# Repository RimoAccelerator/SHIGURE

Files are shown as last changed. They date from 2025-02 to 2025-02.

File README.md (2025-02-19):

# SHIGURE：一款开源的在线控制注射泵

## 背景和原理

输液泵是实验室自动化中最基础的部件之一，而注射泵是所有泵中最容易DIY的（虽然成本不一定最低）。市场上注射泵的价格在500~1000+ RMB左右，相比之下DIY的注射泵更有性价比，不仅能实现相似的功能，还有灵活得多的控制方式，可适配多种自定义的用途。SHIGURE是开源的在线控制注射泵，遵循如下步骤，每个人都能组装出一台可以同时使用Wifi和串口方式控制的注射泵，并且借助客户端可以实现复杂的流程控制、甚至多泵协同工作。

注射泵的核心部件是步进电机和丝杆滑台。步进电机在接收脉冲后旋转，通过丝杆滑台转化为线性位移，只需用固定件将注射器固定在滑台上即可。为了能兼容往复运动以及不同规格和含有不同量液体的注射器，设计了一个用4组螺杆和8个手拧螺母的调节机构，可以在前后上下方向改变注射器卡口的位置。

为了控制步进电机，使用树莓派Pico发送PWM脉冲给TMC2209控制模块后驱动电机运动。在丝杆滑台两端设置限位开关，当滑块运动到尽头时及时停止运动。

为了实现对硬件的操纵，使用带有Wifi功能的树莓派Pico W，同时允许串口控制。

## 目录结构

Models： 3D打印PCB外壳文件；各固定件的图纸文件；

PCB：嘉立创EDA的项目文件和Gerber文件；

ShigureController：控制软件代码；

shigure_main.py：树莓派pico上的micropython代码。

## 精度参数

| 注射器（mL) | 最小流速 （mL/min) | 最大流速 （mL/min) | 流速精度 |
| ------- | ------------- | ------------- | ---- |
| 30      | 0.51          | 200           | ±5%  |
| 10      | 0.20          | 80            | ±3%  |
| 5       | 0.15          | 50            | ±1%  |
| 1       | 0.03          | 10            | ±1%  |

## 物料和成本

以下为直接采购的物料：

| 物料            | 数量  | 型号/供应商                    | 单个成本 (RMB) |
| ------------- | --- | ------------------------- | ---------- |
| 丝杆滑台          | 1   | 1204/100 mm 东台市欧力传动部件有限公司 | 150        |
| 限位开关          | 2   | NPN 海杰嘉创行星减速机工厂           | 15         |
| 树莓派Pico W     | 1   | -                         | 52         |
| TMC2209模块     | 1   | 同拓展志                      | 14         |
| M4螺丝          | 4   | -                         | -          |
| M4螺柱          | 4   | -                         | -          |
| 手拧螺母（羊角）      | 4   | -                         | -          |
| 手拧螺母（圆形）      | 4   | -                         | -          |
| 1 k电阻         | 5   | -                         | -          |
| 二极管           | 2   | IN4148                    | -          |
| LED           | 2   | -                         | -          |
| CH340串口转USB模块 | 1   | -                         | 6          |
| 导线、连接座        | 若干  | -                         | -          |

以上各部件均来自淘宝。树莓派Pico W必须使用原版。

需要制作4个固定件，参考成本：嘉立创3D打印，约25元；嘉立创钣金加工，约70元。

## 机械部分装配过程

1. 打印零件
   
   固定件1
   
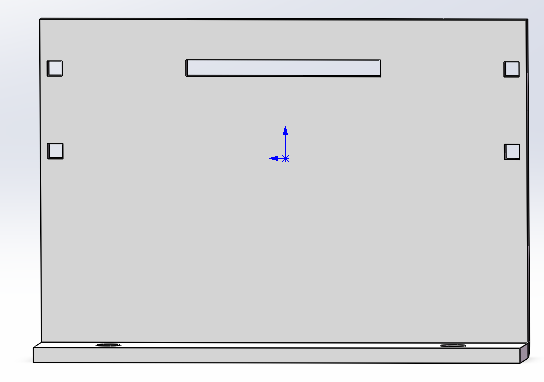
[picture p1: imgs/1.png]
   
   
   固定件2（互为镜像的一对，以下只展示一个）
   
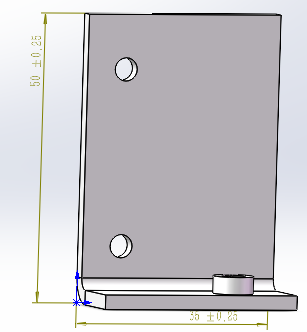
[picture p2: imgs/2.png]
   
   
   固定件3
   
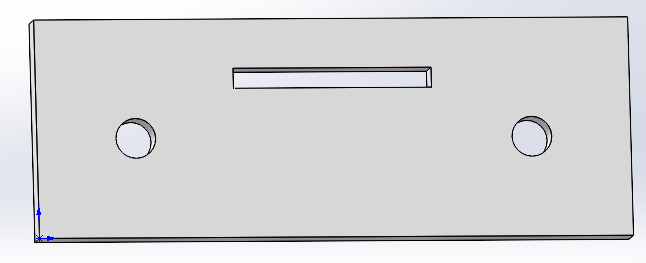
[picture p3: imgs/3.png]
   
   
   固定件4
   
   
   
   关于孔大小：
   
   * 所有孔均设计为M4尺寸。在图纸中，孔直径按照3.3 mm画，如果进行CNC加工可以自动识别为M4螺丝座。如果是3D打印，需将孔直径改成合适的值（至少是4 mm）。
     
     其中固定件4要特别说明。固定件4上的2个螺纹孔位需要插入M4螺柱，且上下没有螺母紧固，需要自身螺纹将螺柱咬住。这是所有打印件里唯一对孔大小有较严格要求的部分。如果使用3D打印加工，图纸上的孔位半径需要根据打印机状态调整，适应公差。例如，开发者自有的3D打印机打出来的孔负公差很大，而嘉立创的3D打印则公差较小。对于前者，此处孔径需要设计为4.4 mm左右，而对于后者可设计为3.8 mm左右，需要尝试和经验。好在对于树脂3D打印器件，无论孔是开得偏大还是偏小都有手动处理的办法，如果孔太大可以用热熔胶将螺柱粘上去，如果孔太小可以用火烧一烧。

2. 安装限位开关
   
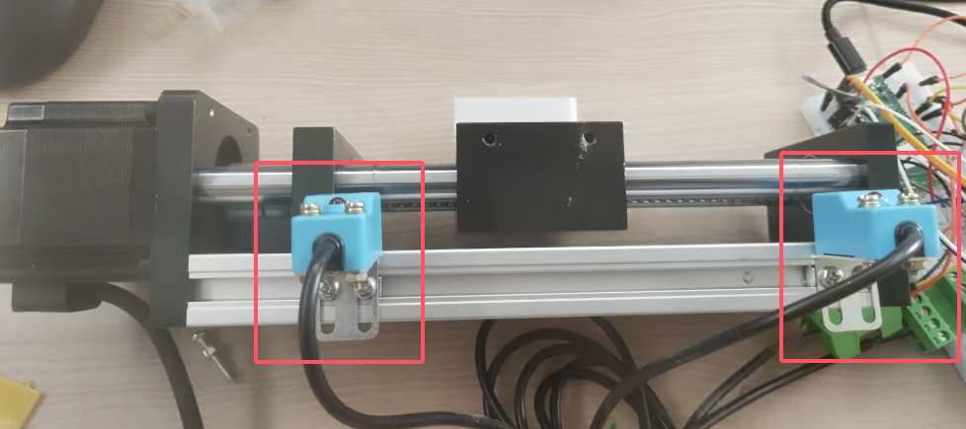
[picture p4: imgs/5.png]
   

3. 安装固定件1，将螺丝打在电机一侧固定端的孔位，在外侧以螺母固定，并利用两侧的孔位安装弹簧。图纸中设计了2个弹簧孔位，至少要在顶部与注射器卡槽平齐的一组安装弹簧。
   
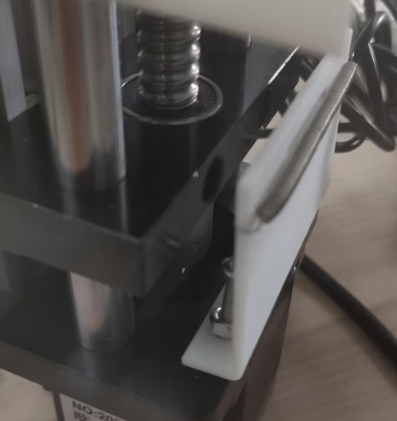
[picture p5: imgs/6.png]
   

4. 在丝杆滑台侧面安装固定件2，将螺丝打进滑块侧面的孔位，在外侧以螺母固定。
   
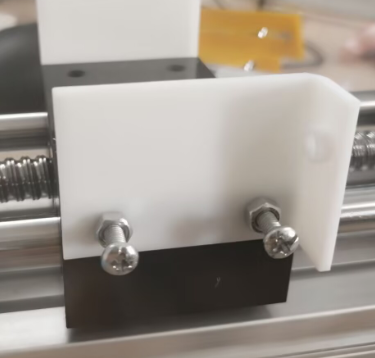
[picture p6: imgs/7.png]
   

5. 通过固定件2，插入M4螺柱，在靠内侧一端以螺母固定，靠外侧一端放入圆形手拧螺母。随后在螺柱上安装固定件4，外侧以羊角手拧螺母固定。这里螺柱的作用是调节注射器活塞卡口位置以适配各种型号、或存有各种体积液体的注射器，因此可以选用足够长的螺柱。作为演示，此处使用了短螺柱。
   
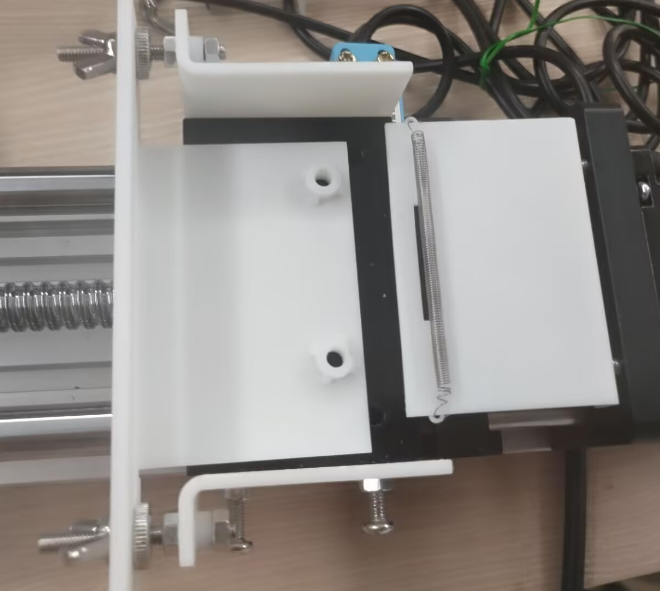
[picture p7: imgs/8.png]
   

6. 在固定件4的两个空位上插入M4螺柱，不使用螺母固定。在螺柱上依次放入圆形手拧螺母、固定件3、羊角手拧螺母。放入注射器，通过调节4组手拧螺母可改变固定件3和4的位置以适应注射器长度和高度。
   
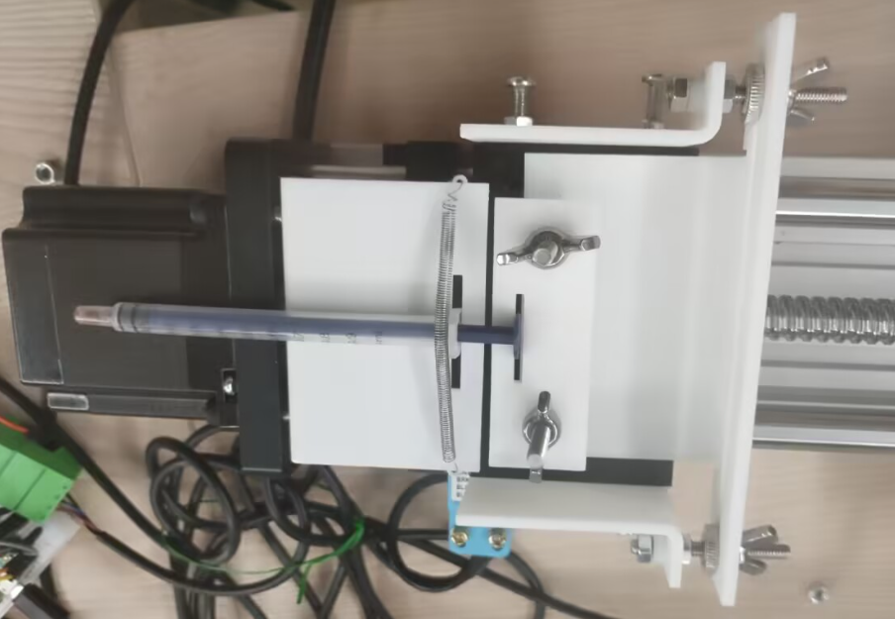
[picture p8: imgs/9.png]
   
   
   以下是使用钣金件的版本，强度更高：
   
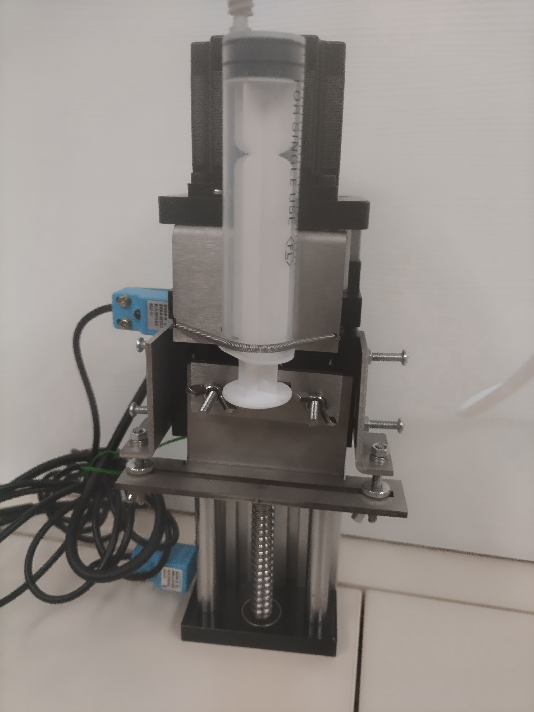
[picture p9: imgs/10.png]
   
   
   ## 电子部分
   
   使用树莓派Pico W进行控制，利用TMC2209驱动电机。以下为原理图：
   
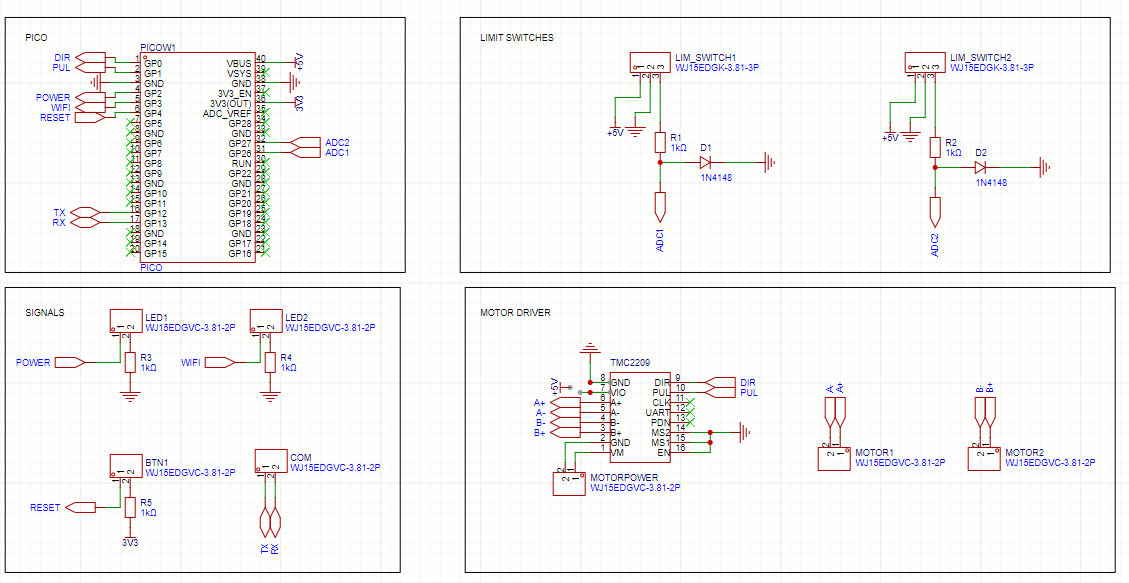
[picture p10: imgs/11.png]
   
   
   TMC2209模块采用Pico的5 V供电，57步进电机使用12 V/2 A的电源。电机电源线和4个线圈连线接在TMC2209上。Pico的GPIO0和1分别用作DIR和PUL，GPIO2~4分别用于控制电源指示灯、控制WIFI指示灯和接收开关按键信号。GPIO12和13留作与上位机通信的串口接口。
   
   两个限位开关使用5 V供电，两个限位开关平时输出5 V电压，在滑块靠近时输出0 V。由于Pico不能直接读取5 V电平，使用二极管钳位电路将限位开关输出的5 V转化为大约0.7 V电位后，通过GPIO26和27进行ADC读取。当这两个引脚的输入电压低于0.5 V时，判定为滑块接近限位开关，停止滑块运动。
   
   在面包板上的连接相对而言是比较简单的：
   
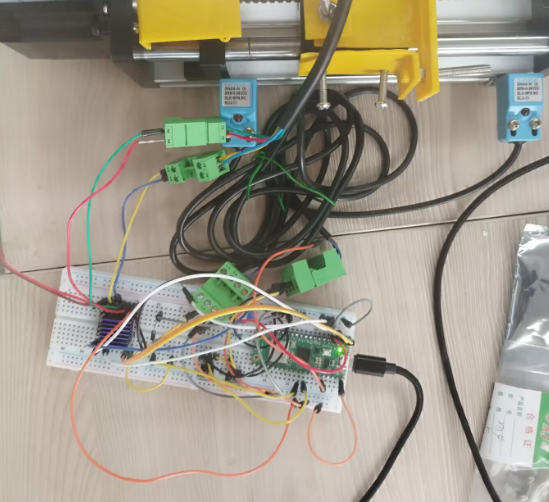
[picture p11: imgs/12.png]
   
   
   以上电路可以转移到一个7.2 * 7.0 cm2的PCB板上：
   
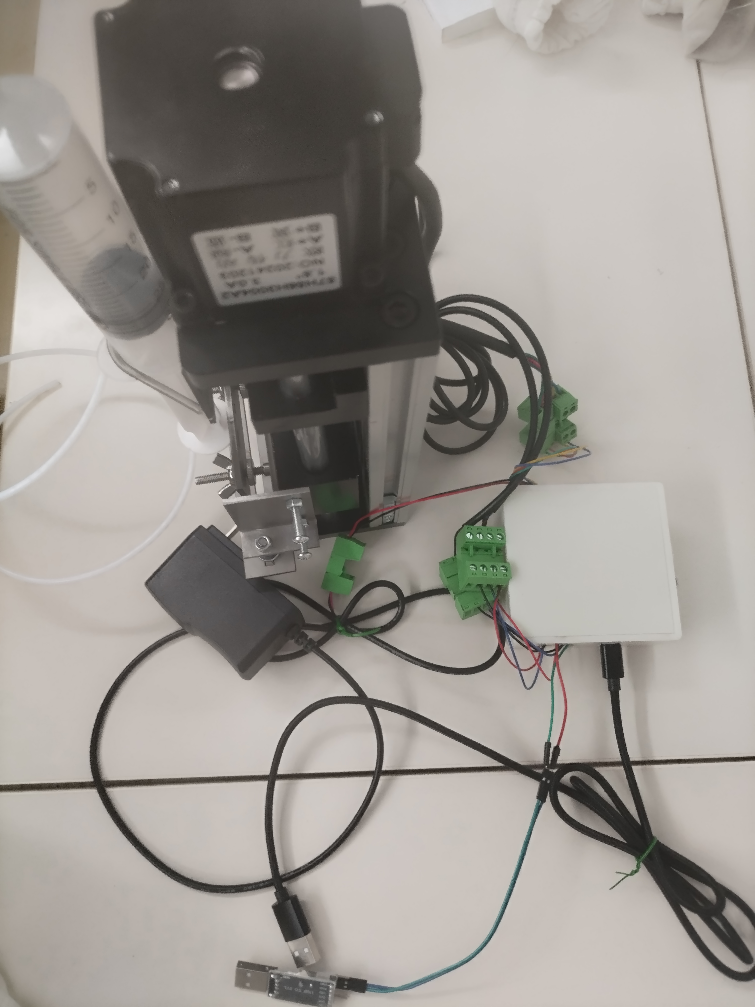
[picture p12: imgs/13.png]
   

## 操作过程

### AP模式

SHIGURE第一次运行时，Wifi处于未配置状态。开始运行后，GP2连接的电源LED亮起，GP3连接的Wifi LED不亮，程序处于AP模式，将产生一个以PumpXX为名称的Wifi信号，其中XX是100以内的随机数。连接这个Wifi（密码是bsjinstrument）后，访问192.168.4.1，进入注射泵控制页面。

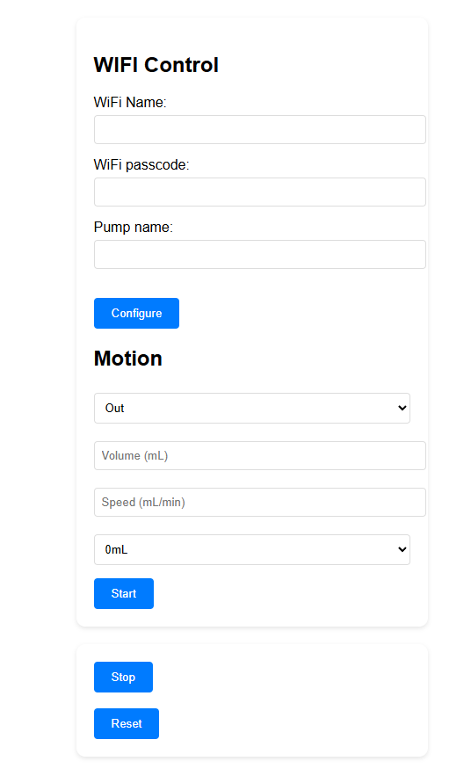
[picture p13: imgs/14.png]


在这一页面，可以输入Wifi信息，点击Configure，则机器将Wifi信息写入存储中并自动重启连接该Wifi，进入Wifi模式，此时GP4连接的Wifi LED亮起。Pump name可以自定义。机器连接Wifi后，AP模式同样可以使用，与此同时，同Wifi内的设备也可以访问注射泵。

如果需要重置，可以长按开关3 s。如果短按，则设备会重启但不重置。

### 网页控制

在网页内的Motion模块，可以选择注射器型号、设置体积和流速。In和Out分别对应吸液和推液。点击Reset后，SHIGURE会推出液体，直到达到限位开关位置。

如果注射器规格选择0 mL，则Volume和Speed分别表示移动的距离（mm）和速度（mm/min)。

### 客户端控制

Wifi模式中，注射泵连接Wifi并获得IP地址。输入注射泵的IP地址后，可以打开相同页面。但一般用户不容易知道注射泵的IP地址，ShigureController客户端提供了控制局域网内所有注射泵的平台。

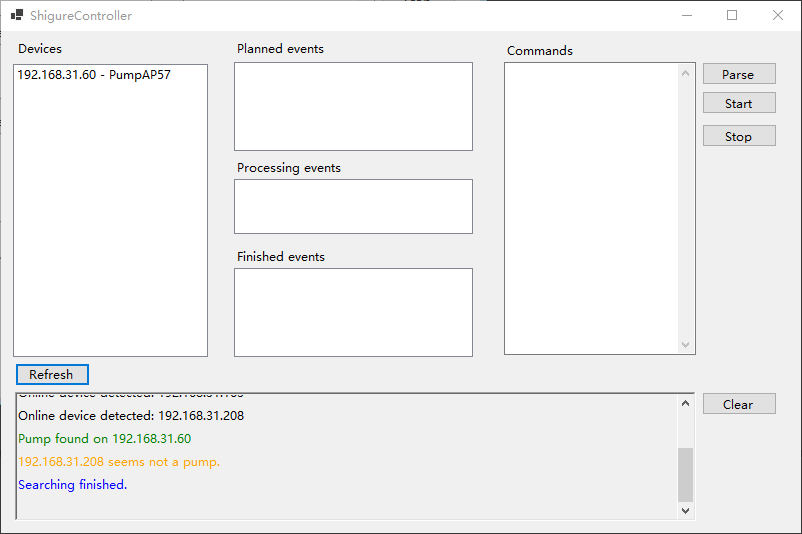
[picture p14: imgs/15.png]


运行ShigureController后，程序会自动搜索局域网内的设备，将注射泵的IP和名称列出。用户在Commands里，按照如下格式输入命令：

```
set ID xx #为相应ID的泵设置注射器规格为xx mL
move ID direction volume speed
    #让相应ID的泵按照给定方向（in或out）以指定流速（mL/min）运行指定体积（mL）
pause ID xx #让相应ID的泵停止xx min
```

以下是一个例子：

```
set PumpAP57 30
move PumpAP57 out 10 200
move PumpAP57 in 10 200
pause PumpAP57 0.1
move PumpAP57 out 10 200
```

在这个例子中，PumpAP57采用30 mL注射器，先以200 mL/min打出10 mL，再吸入10 mL，暂停6 s后再打出10 mL。为了兼容网络延迟，使用客户端控制时，每两个动作之间会有一段3 s的暂停。

当存在多个泵时，可以用类似的方法控制每个泵实现协同工作。（但目前未测试过多泵协同，这是由于只组装了一台）

在输入命令后，首先点击Parse，则这些事件规划进入到Planned events中：

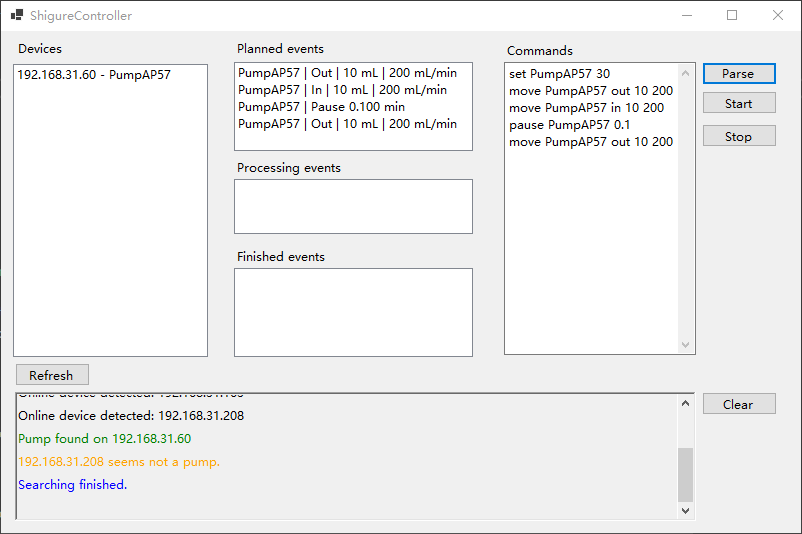
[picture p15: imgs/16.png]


然后点击Start，开始依次执行：

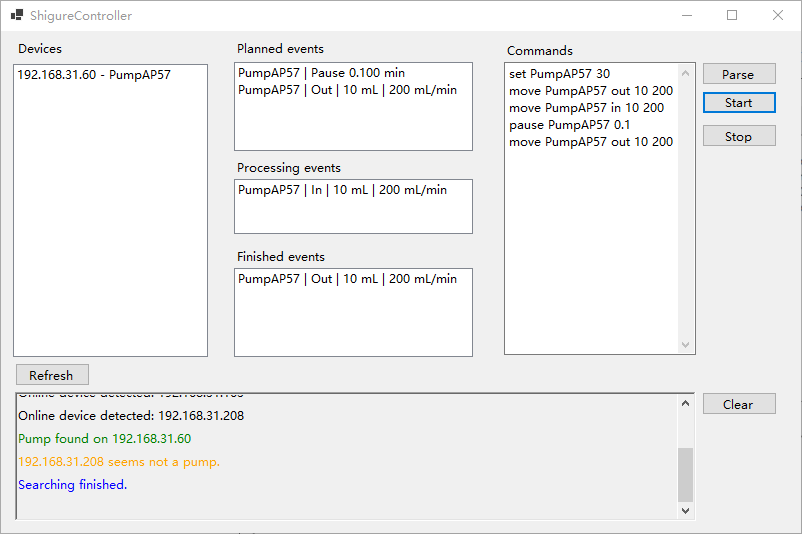
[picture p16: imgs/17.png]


执行完成后，所有事件都将进入到Finished events中。当然也可以随时点击Stop停止流程。

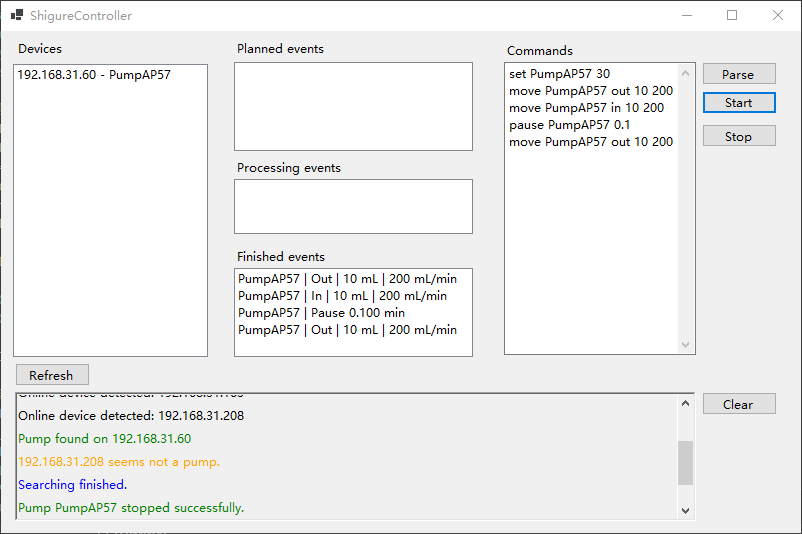
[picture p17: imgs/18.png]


### 串口控制

除了网络控制外，SHIGURE预留了串口线，可以同时接受串口信号，但不会返回信号。波特率采用9600，通信格式为： 

```
set syringe XX #设置注射器规格为XX mL
move direction volume speed 
    #按照给定方向（in或out）以指定流速（mL/min）运行指定体积（mL）
stop #停止
reset #重置
```

## 关于

SHIGURE是BSJ INSTITUTE开发的第二款开源硬件。我们将推出更多开源硬件，推动科学研究的普及化和自由化。

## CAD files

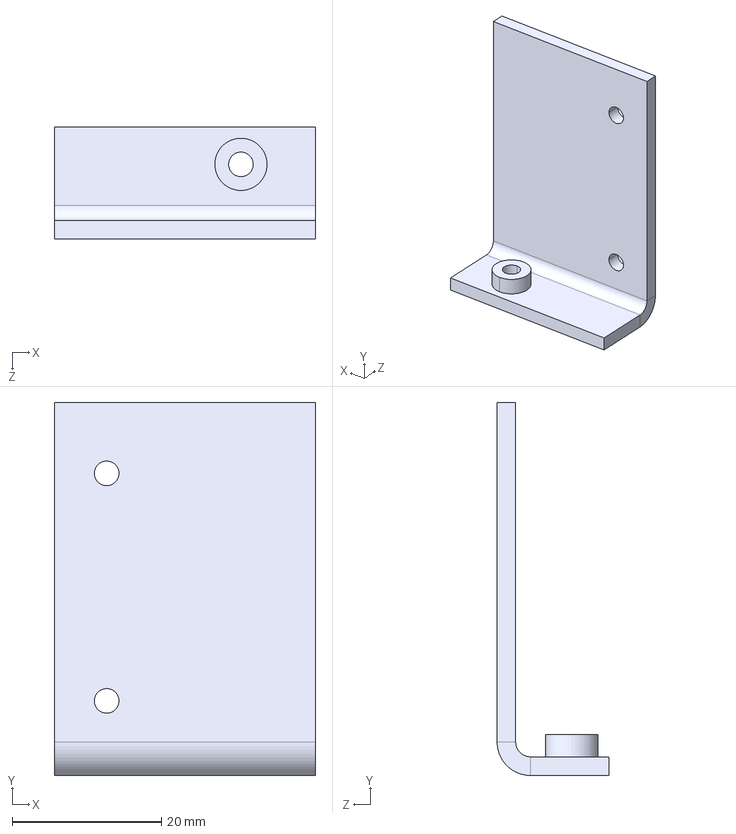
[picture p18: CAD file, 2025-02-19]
a/Models/Mirror_Fixture2.STEP
35.0 x 50.0 x 15.0 mm

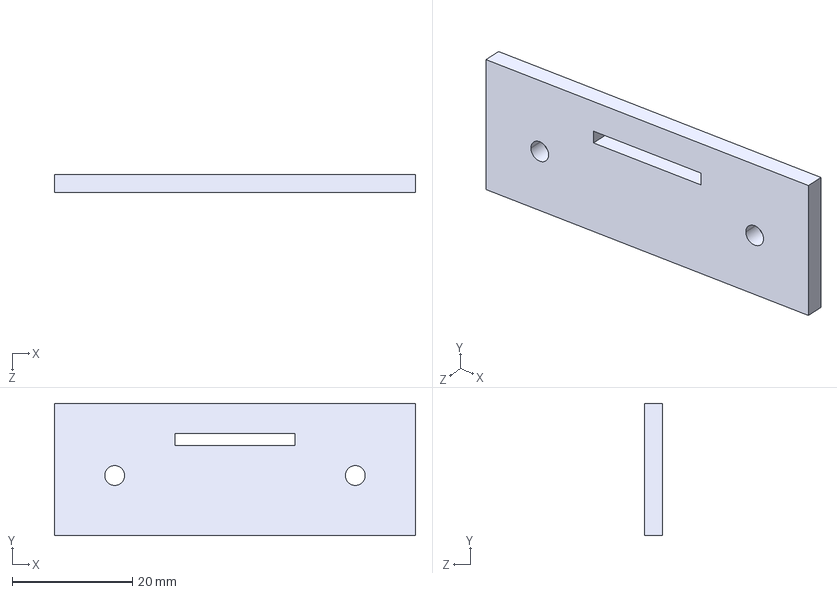
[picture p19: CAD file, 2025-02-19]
Models/Fixture3.STEP
60.0 x 22.0 x 3.00 mm

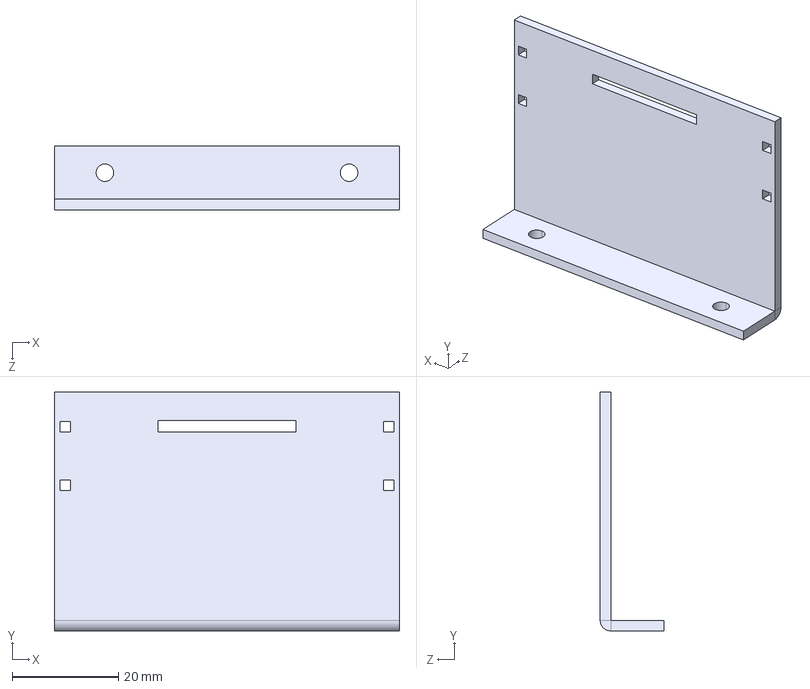
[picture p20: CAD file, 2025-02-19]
a/Models/Fixture1.STEP
65.0 x 45.0 x 12.0 mm

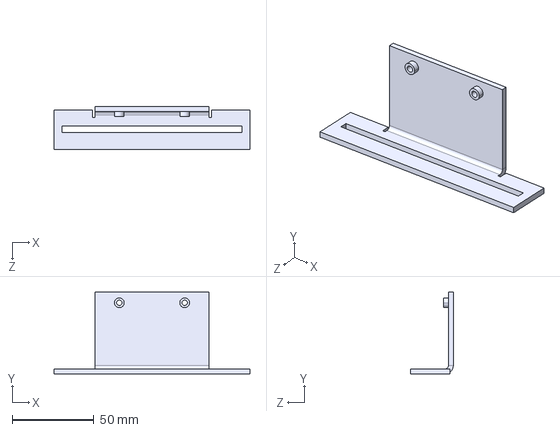
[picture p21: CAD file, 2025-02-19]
a/Models/Fixture4.STEP
120.0 x 50.0 x 26.1 mm

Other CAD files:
a/Models/Fixture2.STEP
Models/Fixture2.STEP
Models/Fixture1.SLDPRT
Models/Fixture2.SLDPRT
Models/Fixture3.SLDPRT
Models/Fixture4.SLDPRT
Models/Mirror_Fixture2.SLDPRT
a/Models/Fixture1.SLDPRT
a/Models/Fixture2.SLDPRT
a/Models/Fixture3.SLDPRT
a/Models/Fixture4.SLDPRT
a/Models/Mirror_Fixture2.SLDPRT

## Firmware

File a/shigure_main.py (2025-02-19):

import network
import machine
import os
import ujson
from machine import Pin, ADC, PWM
import utime
import socket
import ure
import random
import select
import sys
import uselect

# 硬件配置 ====================================================
MOTOR_DIR = Pin(0, Pin.OUT)
MOTOR_PUL = Pin(1, Pin.OUT)
PWM_PUL = PWM(MOTOR_PUL)
PWM_PUL.duty_u16(0)  # 50% duty cycle
PWM_PUL.freq(1000) 
LED_POWER = Pin(2, Pin.OUT)
LED_WIFI = Pin(3, Pin.OUT)
LED_BOARD = Pin("LED", Pin.OUT)

POS_SENSOR1 = ADC(Pin(26))
POS_SENSOR2 = ADC(Pin(27))

SWITCH_PIN = Pin(4, Pin.IN, Pin.PULL_DOWN)

# 运动参数 =====================================================
MICROSTEP = 1
DISTANCE_PER_REV = 0.4 * 1.2  # mm, 1.2 is determined by the actual measurement
STEPS_PER_REV = 200
MAX_SPEED = 500  # mm/min
SYRINGE_PROFILES = {
    0 : 0, 1 : 4.74, 5 : 12.6, 10 : 15.17, 30 : 23.6  # 注射器直径(mm)
}
SYRINGE = 30 # default syringe size
DIRECTION_PULL = 0
DIRECTION_PUSH = 1

# 全局状态 =====================================================
class State:
    IDLE = 0
    MOVING = 1
    STOPPING = 2

motor_state = State.IDLE
frequency = 0
motion_time = 0 # motion time in seconds
start_time = utime.ticks_ms()
direction = DIRECTION_PUSH
emergency_stop = False
switch_pressed_time = 0

# WiFi配置 =====================================================
WIFI_SSID = ''
WIFI_PWD = ''
HOST_NAME = 'PumpAP' + str(random.randint(0,100))
AP_CONFIG = (HOST_NAME, 'bsjinstrument')
CONFIG_FILE = 'wifi.json'

# 电机控制函数 =================================================
def update_motor():
    global motor_state, current_steps, last_step, emergency_stop
    if motor_state != State.MOVING:
        return
    # 碰撞检测
    if (direction == DIRECTION_PUSH and read_sensor(POS_SENSOR1)) or \
       (direction == DIRECTION_PULL and read_sensor(POS_SENSOR2)):
        emergency_stop = True
        print('Motion stopped because obstacle met')
    
    # 紧急停止或完成运动
    if emergency_stop:
        motor_state = State.STOPPING
        PWM_PUL.duty_u16(0)
        motor_state = State.IDLE
        print('Motion stopped because stop signal received')
        emergency_stop = False
        return
    
    # 步进脉冲生成
    now = utime.ticks_ms()
    if utime.ticks_diff(now, start_time) > motion_time * 1000:
        motor_state = State.STOPPING
        PWM_PUL.duty_u16(0)
        motor_state = State.IDLE
        print('Motion stopped because target reached')
        return


def read_sensor(sensor):
    return sensor.read_u16() * 3.3 / 65535 < 0.5 # Return True when sensor value is low, meaning obstacle detected

def calculate_motion(syringe, volume, speed):
    diameter = SYRINGE_PROFILES.get(syringe, 20)
    if syringe == 0:
        distance = volume
    else:
        area = 3.14159 * (diameter/2)**2  # mm²
        distance = (volume * 1000) / area  # mm 
    speed = distance / (volume / speed) / 60 # mm/s
    time = distance / speed  # s
    print(f'distance: {distance} mm, speed: {speed} mm/s, time: {time}')
    frequency = int(speed / DISTANCE_PER_REV * STEPS_PER_REV * MICROSTEP)  # Calculate frequency for PWM
    return frequency, time

def reset_motor():
    global motor_state, direction, frequency, motion_time, PWM_PUL, start_time
    motor_state = State.MOVING
    direction = DIRECTION_PUSH
    MOTOR_DIR.value(direction)
    motion_time = 20
    start_time = utime.ticks_ms()
    PWM_PUL.freq(2000)
    PWM_PUL.duty_u16(32768)

# 网络处理函数 =================================================
class WebServer:
    def __init__(self, ip):
        self.sock = socket.socket()
        self.sock.setsockopt(socket.SOL_SOCKET, socket.SO_REUSEADDR, 1)
        self.sock.bind(('0.0.0.0', 80))
        self.sock.listen(5)
        #self.sock.settimeout(0.1)
        self.sock.setblocking(False)
        self.routes = {
            r'GET /': self.handle_root,
            r'POST /move': self.handle_move,
            r'POST /stop': self.handle_stop,
            r'POST /reset': self.handle_reset,
            r'POST /configure': self.handle_configure
        }
        self.poll = select.poll()
        self.poll.register(self.sock, select.POLLIN)  # 使用poll机制
    
    def process(self):
        res = self.poll.poll(50)  # 50ms超时
        for sock, event in res:
            if sock == self.sock:
                try:
                    cl, addr = self.sock.accept()
                    cl.setblocking(False)
                    self.poll.register(cl, select.POLLIN)
                except OSError:
                    pass
            else:
                self.handle_client(sock)

    def handle_client(self, cl):
        try:
            request = cl.recv(1024).decode()
            if request:  # 确保收到有效请求
                self.handle_request(cl, request)
        except Exception as e:
            print('Client error:', e)
        finally:
            self.poll.unregister(cl)
            cl.close()
    
    def handle_request(self, cl, request):
        for pattern, handler in self.routes.items():
            if ure.match(pattern, request):
                return handler(cl, request)
        self.send_response(cl, "Not Found", status=404)
    
    def handle_root(self, cl, request):
        options = ''.join(f'<option value="{k}">{k}mL</option>' for k in sorted(SYRINGE_PROFILES))
        form = f"""
        <div class="card">
        <h2>WIFI Control</h2>
        <form action="/configure" method="post" enctype="application/x-www-form-urlencoded">
            <label for="ssid">WiFi Name:</label><br>
            <input type="text" id="ssid" name="ssid" value={WIFI_SSID}><br>
            <label for="password">WiFi passcode:</label><br>
            <input type="text" id="password" name="password" value={WIFI_PWD}><br>
            <label for="name">Pump name:</label><br>
            <input type="text" id="name" name="name" value={HOST_NAME}><br>
            <br>
            <button type="submit">Configure</button>
        </form>
          <h2>Motion</h2>
          <form action="/move" method="post" target="hidden-form">
            <select name="dir"><option value="1">Out</option><option value="0">In</option></select>
            <input type="number" name="vol" placeholder="Volume (mL)" step="0.01" required>
            <input type="number" name="speed" placeholder="Speed (mL/min)" min="0"  step="0.01" max={MAX_SPEED} required>
            <select name="syr">{options}</select>
            <button type="submit">Start</button>
          </form>
        </div>
        <div class="card">
          <form action="/stop" method="post" target="hidden-form"><button>Stop</button></form><br />
          <form action="/reset" method="post" target="hidden-form"><button type="button" onclick="this.form.submit()">Reset</button></form>
        </div>
        """
        self.send_response(cl, """<!DOCTYPE html>
<html><head>
<title>Pump Control</title>
<meta name="viewport" content="width=device-width, initial-scale=1">
<style>
  body{max-width:400px;margin:20px auto;padding:20px;font-family:Arial,sans-serif}
  .card{padding:20px;border-radius:10px;box-shadow:0 2px 5px rgba(0,0,0,0.1);margin-bottom:20px}
  input,select{width:100%;padding:8px;margin:5px 0 15px;border:1px solid #ddd;border-radius:4px}
  button{background:#007bff;color:white;border:none;padding:10px 20px;border-radius:4px;cursor:pointer}
  button:disabled{background:#6c757d}
</style>
</head><body><iframe style="display:none" name="hidden-form"></iframe>
""" + form + "</body></html>")
    
    def handle_move(self, cl, request):
        global motor_state, direction, frequency, motion_time, PWM_PUL, start_time, SYRINGE
        params = self.parse_params(request)
        try:
            SYRINGE = int(params.get('syr',20))
            volume = float(params.get('vol',0))
            speed = min(MAX_SPEED, float(params.get('speed',1)))
            direction = int(params.get('dir',0))
            print(f"Move: {direction}, {volume}mL, {speed}mL/min, {SYRINGE}mL syringe")
            frequency, motion_time = calculate_motion(SYRINGE, volume, speed)
            motor_state = State.MOVING
            MOTOR_DIR.value(direction)
            start_time = utime.ticks_ms()
            PWM_PUL.freq(frequency)
            PWM_PUL.duty_u16(32768)
            print(f'Moving: {frequency}Hz, {motion_time}s')
            self.send_response(cl, "Motion start")
        except Exception as e:
            self.send_response(cl, f"Parameter error: {str(e)}", status=400)
    
    def handle_configure(self, cl, request):
        global WIFI_SSID, WIFI_PWD, HOST_NAME
        params = self.parse_params(request)
        try:
            WIFI_SSID = params.get('ssid', '')
            WIFI_PWD = params.get('password', '')
            HOST_NAME = params.get('name', '')
            with open(CONFIG_FILE, 'w') as f:
                ujson.dump({'ssid': WIFI_SSID, 'password': WIFI_PWD, 'name': HOST_NAME}, f)
            ipaddress = connect_wifi(WIFI_SSID, WIFI_PWD)
            print(ipaddress)
            if ipaddress != False:
                self.send_response(cl, f"""
WiFi configured! Now you can connect to the pump at: {ipaddress} within the WiFi you set. <br>
Now the AP mode is to be disabled.
                               """)
                utime.sleep(1)
                disable_ap_mode()
            else:
                raise Exception('WiFi connection failed')
        except Exception as e:
            self.send_response(cl, f"Parameter error: {str(e)}", status=400)

    def handle_stop(self, cl, request):
        global emergency_stop
        print('Stop signal received')
        emergency_stop = True
        self.send_response(cl, "Stopped")
    
    def handle_reset(self, cl, request):
        reset_motor()
        self.send_response(cl, "Reset")
    
    def parse_params(self, request):
        params = {}
        if '\r\n\r\n' in request:
            body = request.split('\r\n\r\n')[1]
            pairs = body.split('&')
            for pair in pairs:
                if '=' in pair:
                    key, value = pair.split('=')
                    params[key] = value
        return params
    
    def send_response(self, cl, msg, status=200):
        cl.send(f"HTTP/1.1 {status} OK\r\nContent-Type: text/html\r\n\r\n{msg}")

# Function to delete all .json files
def reset_wifi():
    for file in os.listdir():
        if file.endswith(".json"):
            os.remove(file)
    print("Wifi information cleared.")

import re
def handle_serial_data(data):
    global motor_state, direction, frequency, motion_time, PWM_PUL, start_time, SYRINGE, emergency_stop
    # Remove any whitespace, newlines, or carriage returns
    data = data.decode().strip().lower()
    # Check for 'set syringe' command
    match = re.match(r'set syringe (\d+)', data)
    
    if match:
        SYRINGE = int(match.group(1))
        return
    # Check for 'move direction volume speed' command
    match = re.match(r'move (in|out) (\d+(\.\d+)?) (\d+(\.\d+)?)', data)
    if match:
        direction = match.group(1)
        volume = float(match.group(2))
        speed = float(match.group(4))
        frequency, motion_time = calculate_motion(SYRINGE, volume, speed)
        motor_state = State.MOVING
        MOTOR_DIR.value(DIRECTION_PULL if direction == 'in' else DIRECTION_PUSH)
        start_time = utime.ticks_ms()
        PWM_PUL.freq(frequency)
        PWM_PUL.duty_u16(32768)
        print(f'Moving: {frequency}Hz, {motion_time}s')
        return
    if data == 'stop':
        emergency_stop = True
        return
    if data == 'reset':
        reset_motor()
        return
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
